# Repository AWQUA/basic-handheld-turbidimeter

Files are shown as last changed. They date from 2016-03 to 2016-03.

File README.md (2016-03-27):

#Basic Handheld Turbidimeter
##Purpose  
The Basic Handheld Turbidimeter is designed to measure turbidity on demand, portably, for the lowest possible price.  

##Function  
_How does the device measure a parameter?_  
This device is a single-beam [nephelometrer](https://en.wikipedia.org/wiki/Nephelometer). Light from an infrared light-emitting diode (IR LED) is scattered by suspended sediment as it passes through a sample of water. This scattered light is detected by an IR-sensitive [photodiode](https://en.wikipedia.org/wiki/Photodiode) mounted at a right angle to the center of the IR LED's light beam. The intensity of light detected by the photodiode is referenced to a calibration curve stored in the device's memory to interpolate the corresponding turbidity value, measured in [nephelometric turbidity units (NTU)](http://or.water.usgs.gov/grapher/fnu.html).  

_How does the device record data?_  
This device is intended for basic manual operation and does not contain storage for data.   

_How does the device display data?_  
The microcontroller at the heart of this device reads the frequency of pulses transmitted by the [photodiode unit](http://www.mouser.com/ProductDetail/ams/TSL230BRD-TR/?qs=sGAEpiMZZMu97qiQi8P%252buifvOPr%252b402N67DKHn09PFo%3d), interpolates the turbidity value from stored calibration data, and displays the turbidity value on a [four-digit display panel](http://www.electrodragon.com/product/7-segment-4-digit-display-common-anode/) (much like those used in some alarm clocks).

_What units does the device report in?_  
Like all AWQUA turbidimeters, this device reports readings in  [nephelometric turbidity units (NTU)](http://or.water.usgs.gov/grapher/fnu.html).  

_How does the device communicate data electronically?_  
This device does not possess data telemetry capabilities.  

##Use Case  
_Where can the device be safely used?_  
This device can handle temperatures up to 70C, and is intended for field conditions. It is not water proof or water resistent, however.

##Power  
_How is the device powered?_  
This device uses 3.3V DC power, and requires less than 100mA of current. A standard 3.7V lithium ion or polymer battery, or three AA alkaline batteries, would suffice to power it.

_How much power does it use?_  
In semi-automated testing, this device was capable of taking 5000 measurements on one set of three AA batteries.

##Standard and Testing  
_How was the device tested?_  
Testing procedures for this device are described in full in [An Affordable Open-Source Turbidimeter](http://www.mdpi.com/1424-8220/14/4/7142).

_How did it perform?_  
Testing results for this device are described in full in [An Affordable Open-Source Turbidimeter](http://www.mdpi.com/1424-8220/14/4/7142). The figure below shows the performance of this model of device, versus a popular commercial turbidimeter.  
"Basic Handheld Turbidimeter evaluated against commercial equivalent"

_What performance standards does the device meet?_  
This device was designed and successfully tested to reliably measure turbidity values well below 1.0 NTU, which is the maximum turbidity value recommended by the World Health Organization for drinking water prior to disinfection. Please note however that this device is not certified to meet EPA requirements for the routine turbidity monitoring of treated drinking water in the United States. 

_What monitoring standards can this device be used to meet?_  
This device is one of several proven turbidimeter designs out there that can be used to meet international and World Health Organization guidelines on turbidity monitoring, yet are not able to meet the very exacting (and expensive) American and European turbidity detection standards. There is an urgent global need for simple, affordable turbidity detection, and AWQUA members are working to establish alternative turbidity detection standards to address this need. Please check out our [Standards](https://github.com/AWQUA/Standards) repository for more information.

##Construction  

###Bill of Materials
| Quantity  | Part Description | Example Price (each) |
| :-------------: | ------------- | :-------------: |
| 1 | ATMega328P-PU microprocessor  | [$2.90](http://www.electrodragon.com/product/atmega328-with-arduino-optiboot-uno/)|
| 1 | 4-digit, 7-segment display  | [$2.10](http://www.electrodragon.com/product/7-segment-4-digit-display-common-anode/)|
| 1 | 74HC595 shift register  | [$0.62](http://www.mouser.com/ProductDetail/Texas-Instruments/SN74HC595N/?qs=sGAEpiMZZMuyBeSSR239IeaeNSzgQbS%2f1btldJdqa6k%3d) |
| 1 | LMT86 temperature sensor  | [$1.00](http://www.mouser.com/ProductDetail/Texas-Instruments/LMT86LP/?qs=sGAEpiMZZMvfFCidbTccA1jyVRrxk5nB%252bTEjPRynSGM%3d)|
| 1 | TSL230BRD  | [$4.83](http://www.mouser.com/ProductDetail/ams/TSL230BRD-TR/?qs=sGAEpiMZZMu97qiQi8P%252buifvOPr%252b402N67DKHn09PFo%3d)|
| 1 | LF33ABV 3.3V Voltage regulator  | [$1.03](http://www.mouser.com/ProductDetail/STMicroelectronics/LF33ABV/?qs=sGAEpiMZZMsGz1a6aV8DcBQiArhhid1gDswAeAw%2fIB0%3d)|
| 2 | 10uF aluminum electrolytic capacitors  | [$0.24](http://www.mouser.com/ProductDetail/Nichicon/ULD1J100MDD1TD/?qs=sGAEpiMZZMvwFf0viD3Y3c1N%2fF%2fpDmX12XlNW9X9Y3vZmYyMo5GpOw%3d%3d)|
| 2 | 22pF ceramic capacitors  | [$0.03](http://www.mouser.com/ProductDetail/Vishay-BC-Components/K220J10C0GF5UH5/?qs=sGAEpiMZZMsh%252b1woXyUXj9nJp%252b8gphztXIKBUu3gv%252bs%3d)|
| 5 | 100nF ceramic capacitors  | [$0.06](http://www.mouser.com/ProductDetail/Vishay-BC-Components/K104Z15Y5VE5TL2/?qs=sGAEpiMZZMsh%252b1woXyUXj5VNmf0jXPWIrWjnp1zAXac%3d)|
| 4 | 100 ohm resistors  | [$0.10](http://www.mouser.com/ProductDetail/KOA-Speer/MOS1-2CT52R101J/?qs=sGAEpiMZZMtlubZbdhIBICYVxaT5CDYBpEIIN%2f0BoAk%3d)|
| 1 | 220 ohm resistors  | [$0.10](http://www.mouser.com/ProductDetail/KOA-Speer/MOS1-2CT52R221J/?qs=sGAEpiMZZMtlubZbdhIBICYVxaT5CDYBStqm8FrIljg%3d)|
| 1 | 1K ohm resistors 1% tolerance | [$0.10](http://www.mouser.com/ProductDetail/Vishay-Beyschlag/MBB02070C1001FCT00/?qs=sGAEpiMZZMtlubZbdhIBIAA6NYEPHyksoxlYyK2s%252btM%3d)|
| 4 | 10K ohm resistors  | [$0.10](http://www.mouser.com/ProductDetail/Vishay-Beyschlag/MBA02040C1002FCT00/?qs=sGAEpiMZZMtlubZbdhIBIP7908E9uONJr6Tgqqo7oLA%3d)|
| 1 | IR LED  | [$0.47](http://www.mouser.com/ProductDetail/Kingbright/WP7113SF4C/?qs=sGAEpiMZZMvAL21a%2fDhxMro1KOf4QOs%252bCw5JRgjZK8o%3d)|
| 1 | LED lighting driver | [$0.54](http://www.mouser.com/Search/ProductDetail.aspx?R=AL5809-30S1-7virtualkey62110000virtualkey621-AL5809-30S1-7)|
| 1 | Momentary contact button  | [$0.91](http://www.mouser.com/ProductDetail/Mountain-Switch/104-0013-EVX/?qs=sGAEpiMZZMvxtGF7dlGNpr35VnaTB25ys95hy84%252ba4o%3d)|
| 1 | SPST power switch  | [$1.15](http://www.mouser.com/ProductDetail/CHERRY/TRG22F2FBBNN/?qs=sGAEpiMZZMtNT9UGfLL4eOd3cDQgL8vM5i2VNLX9H3E%3d)|
| 100 | Header pins (0.1" spacing)  | [$.00225](http://www.electrodragon.com/product/break-away-header/)|
|||
||**Total Cost:**|**$17.61**|
###Circuit Board
####Schematic
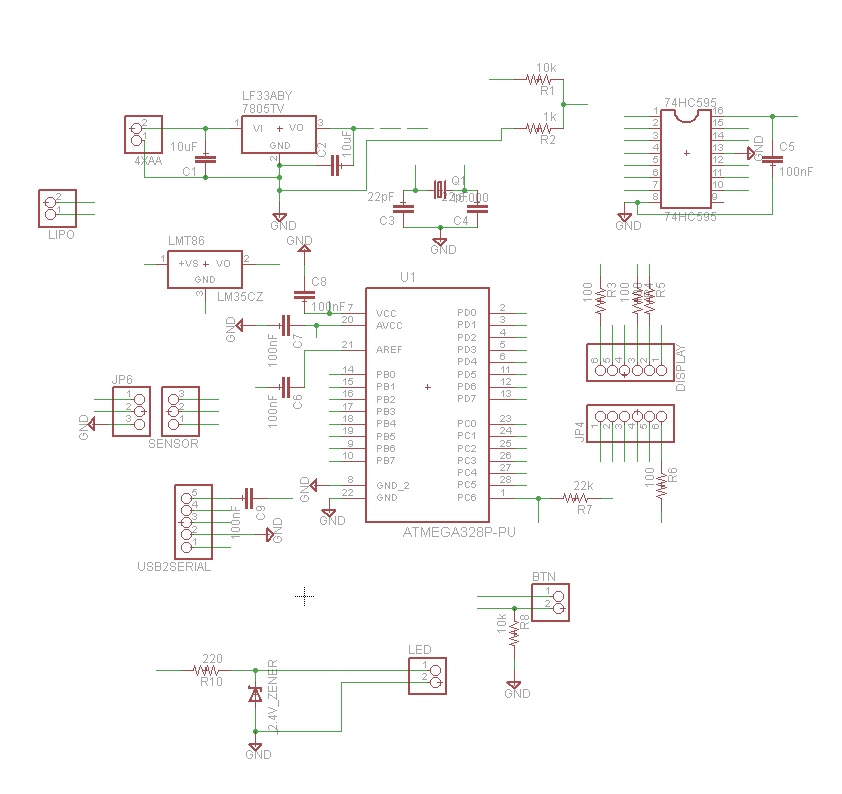
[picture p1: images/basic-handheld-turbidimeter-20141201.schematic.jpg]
picture alt Schematic of Basic Handheld Turbidimeter circuit board [2014-12-01]

####Layout
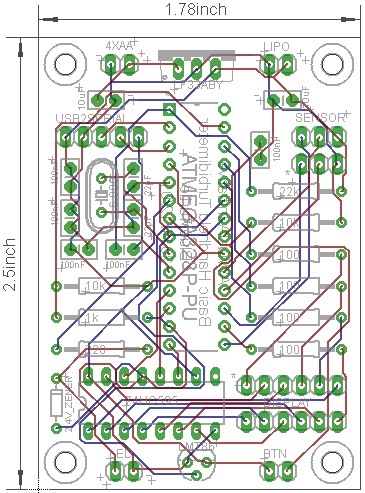
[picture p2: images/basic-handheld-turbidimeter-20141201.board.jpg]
picture alt Layout of Basic Handheld Turbidimeter circuit board [2014-12-01]

###Assembly
For assembly instructions, see the [Supplementary Materials](http://www.mdpi.com/1424-8220/14/4/7142/s1) for An Affordable Open-Source Turbidimeter.  
##FAQ and Troubleshooting  
###Online Resources

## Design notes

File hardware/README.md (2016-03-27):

#Hardware
There are up to three boards in the `basic-handheld-turbidimeter`: the main board (housing the microprocessor), a sensor board that connects to the main board through 0.1" header pins, and an optional third board that lets the display plug directly in to the main board.

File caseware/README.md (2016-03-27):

#Caseware
The caseware for the `basic-handheld-turbidimeter` is provided as an SVG file and a FreeCAD python macro (FCMacro) -- the first file may be viewed and edited in many vector graphics programs (e.g. [Inkscape](https://inkscape.org/en/)), and the latter in [FreeCAD](http://www.freecadweb.org/).  
  
This case is designed for 0.25"-thick acryllic; suitable alternative materials exist. It is recommended that the case be cut from an opaque material to prevent background light leakage onto the turbidity sensor (though can be programmed to compensate for this to an extent), with the exception of the `case_top_cover` piece (bottom left in the SVG layout) which should be cut from a clear material so that the LED display underneath it is visible to the user.

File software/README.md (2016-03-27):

#Software
The software for this device is kept here; it requires the following external libraries to compile properly:

[`EEPROM`](https://www.arduino.cc/en/Reference/EEPROM)
[`EEPROMWriteAnything.h`](http://playground.arduino.cc/Code/EEPROMWriteAnything)
[`PinChangeInt`](http://playground.arduino.cc/Main/PinChangeInt)

To edit this code in the [Arduino IDE](https://www.arduino.cc/en/Main/Software), copy the folder named basic-handheld-turbidimeter into your Arduino sketchbook.

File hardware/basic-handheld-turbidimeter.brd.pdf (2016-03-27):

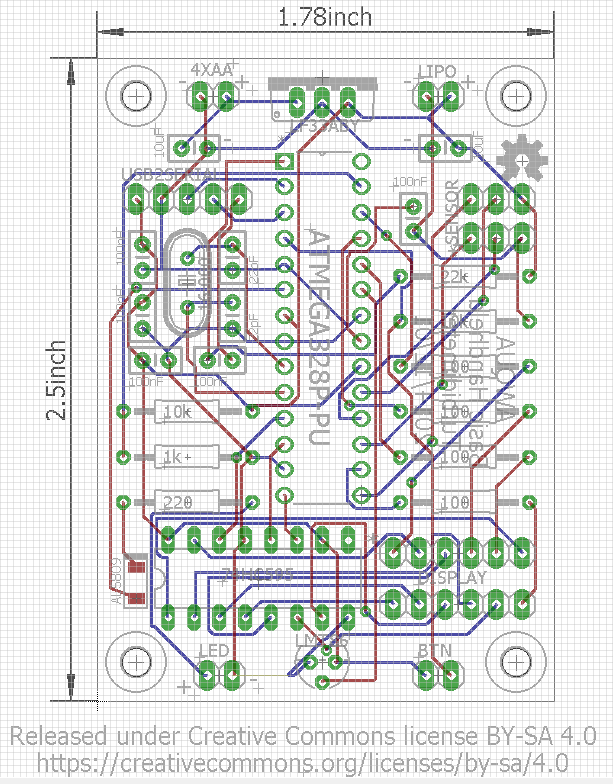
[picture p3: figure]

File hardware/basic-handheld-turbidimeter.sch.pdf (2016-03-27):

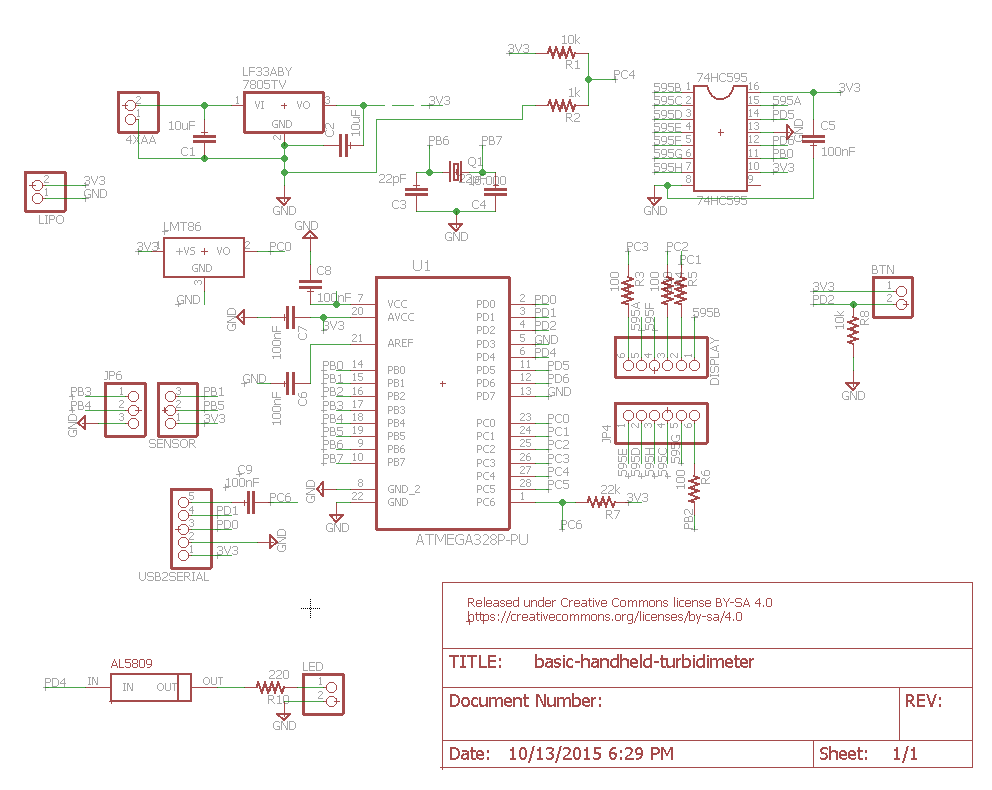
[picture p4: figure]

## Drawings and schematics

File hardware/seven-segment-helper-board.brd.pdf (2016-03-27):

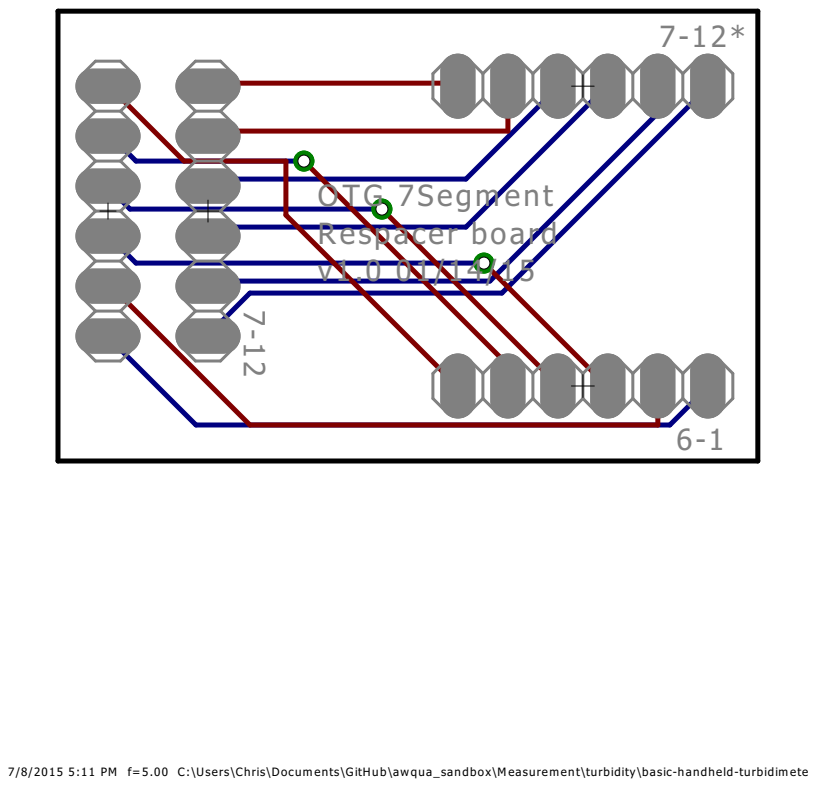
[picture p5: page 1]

7/8/2015 5:11 PM f=5.00 C:\Users\Chris\Documents\GitHub\awqua_sandbox\Measurement\turbidity\basic-handheld-turbidimeter\hardware\seven-segment-helper-boardsch.brd

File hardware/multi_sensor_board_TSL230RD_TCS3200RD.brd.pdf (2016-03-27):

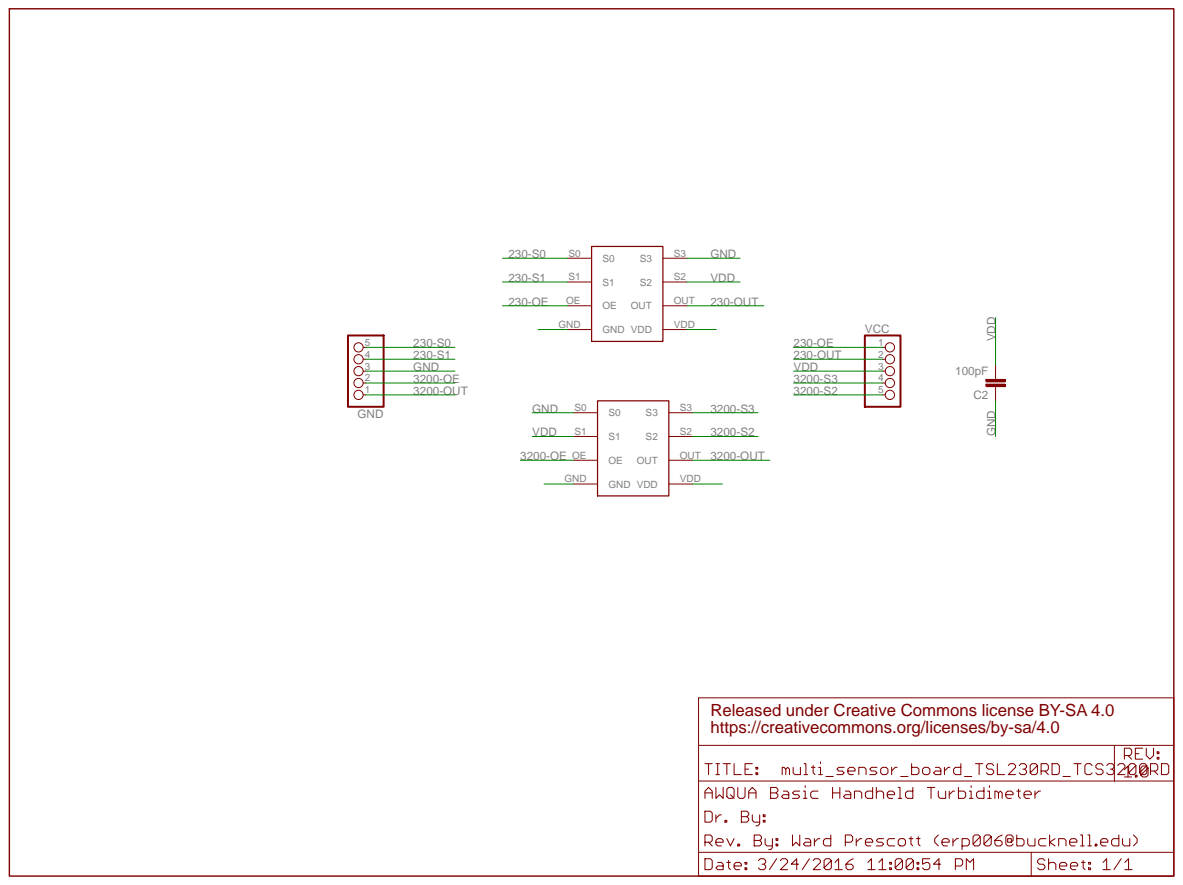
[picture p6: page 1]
GND GND; OUT; VDD; GND; VCC 1 2 3 4; 230-OUT; 3200-OUT

Released under Creative Commons license BY-SA 4.0
https://creativecommons.org/licenses/by-sa/4.0

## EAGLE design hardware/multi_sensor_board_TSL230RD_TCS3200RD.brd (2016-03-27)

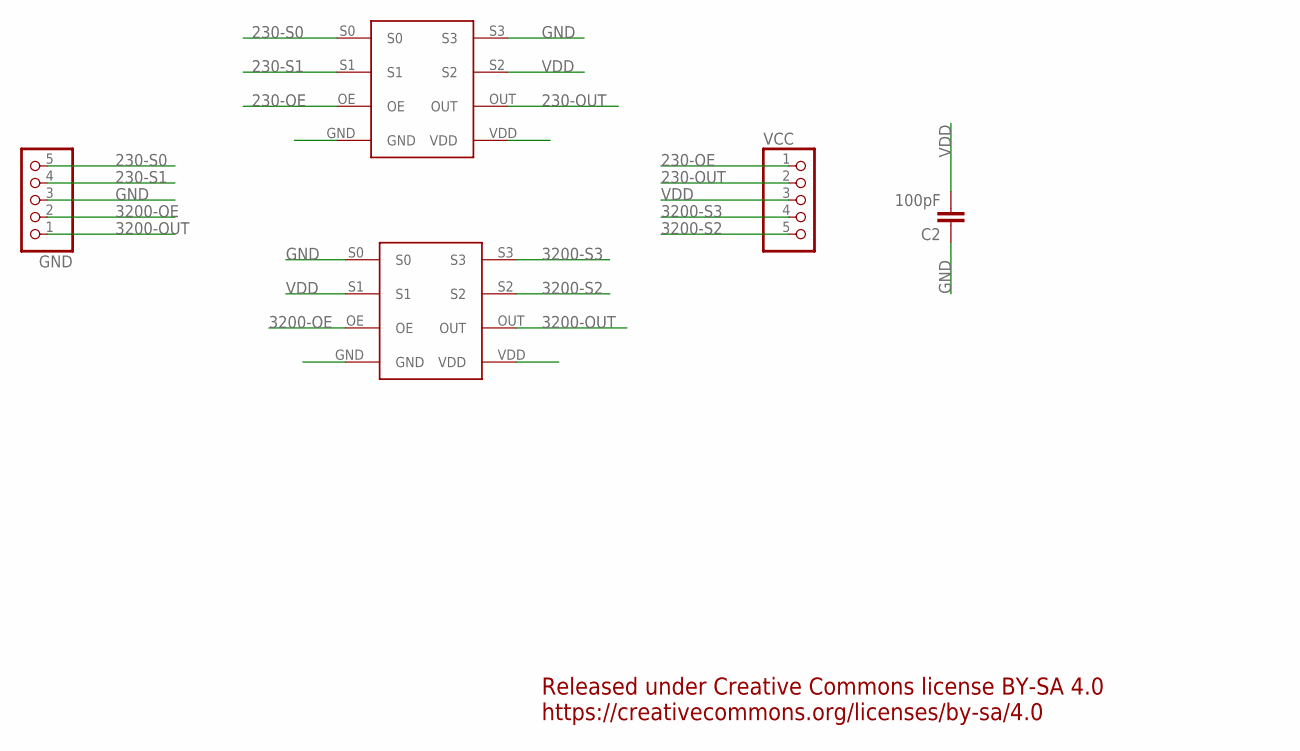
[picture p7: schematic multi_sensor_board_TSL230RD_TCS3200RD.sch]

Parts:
C2: 100pF; 0805
COLOR: TCS3200RD; TSL230RD
GND: PINHD-1X5; 1X05
IR: TSL230R; TSL230RD
VCC: PINHD-1X5; 1X05

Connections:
230-OE: IR.OE, VCC.1
230-OUT: IR.OUT, VCC.2
230-S0: GND.5, IR.S0
230-S1: GND.4, IR.S1
3200-OE: COLOR.OE, GND.2
3200-OUT: COLOR.OUT, GND.1
3200-S2: COLOR.S2, VCC.5
3200-S3: COLOR.S3, VCC.4
GND: C2.1, COLOR.GND, COLOR.S0, GND.3, IR.GND, IR.S3
VDD: C2.2, COLOR.S1, COLOR.VDD, IR.S2, IR.VDD, VCC.3

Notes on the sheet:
Released under Creative Commons license BY-SA 4.0 https://creativecommons.org/licenses/by-sa/4.0

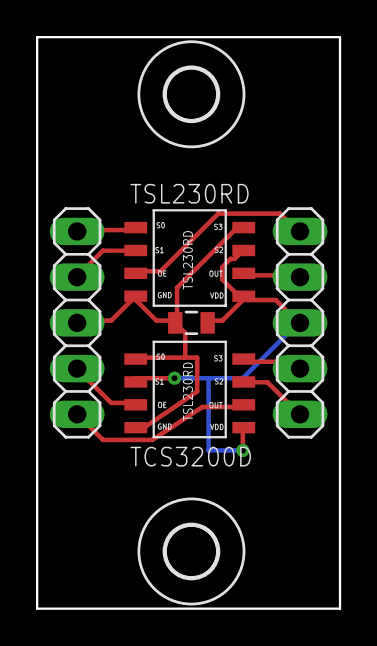
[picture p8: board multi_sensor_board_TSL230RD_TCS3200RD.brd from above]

Board: 2 copper layers, 16.8 x 31.8 mm, 7 parts (0 on the bottom side), 10 nets.

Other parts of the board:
U$1, U$2: 2,8

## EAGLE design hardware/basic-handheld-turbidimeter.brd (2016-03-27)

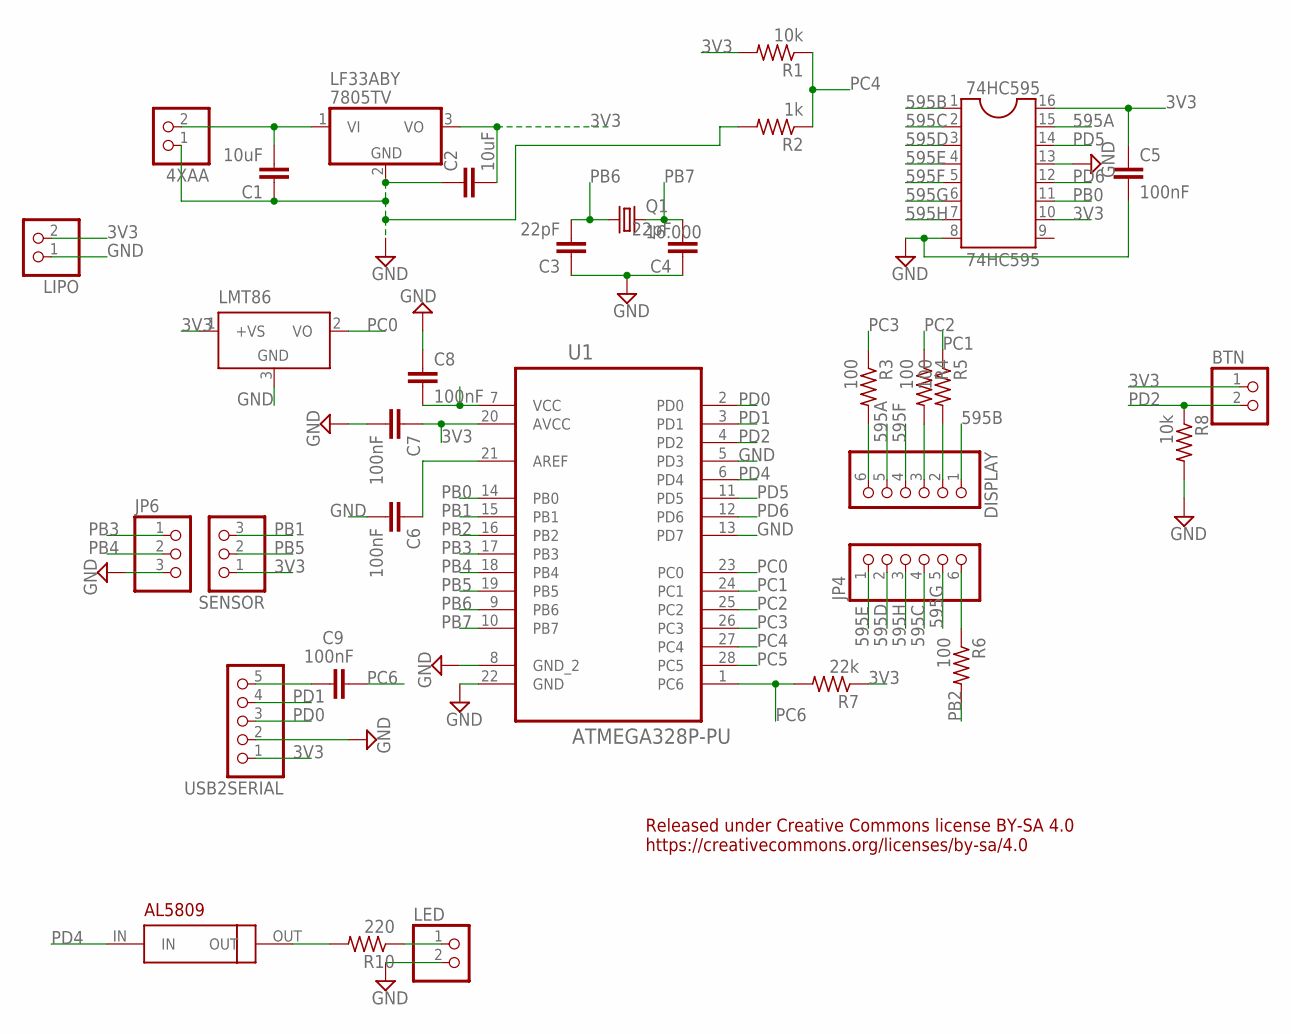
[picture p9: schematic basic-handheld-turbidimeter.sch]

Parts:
4XAA: PINHD-1X2; 1X02
74HC595: 74HC595; DIL16
BTN: PINHD-1X2; 1X02
C1, C2: 10uF; CAP-PTH-SMALLEZ
C3, C4: 22pF; CAP-PTH-SMALLEZ
C5, C6, C7, C8, C9: 100nF; CAP-PTH-SMALLEZ
DISPLAY: PINHD-1X6; 1X06
JP4: PINHD-1X6; 1X06
JP6: PINHD-1X3; 1X03
LED: PINHD-1X2; 1X02
LF33ABY: 7805TV; TO220V
LIPO: PINHD-1X2; 1X02
LMT86: LM35CZ; TO92
Q1: 16.000; HC49/S
R1, R8: 10k; 0207/12
R2: 1k; 0207/12
R3, R4, R5, R6: 100; 0207/12
R7: 22k; 0207/12
R10: 220; 0207/12
SENSOR: PINHD-1X3; 1X03
U1: ATMEGA328P-PU; DIP254P762X457-28
U$6: AL5809
USB2SERIAL: PINHD-1X5; 1X05

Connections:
3V3: 74HC595.10, 74HC595.16, BTN.1, C2.2, C5.1, C7.1, C8.2, LF33ABY.3 (VO), LIPO.2, LMT86.1 (+VS), R1.2, R7.1, SENSOR.1, U1.7 (VCC), U1.20 (AVCC), USB2SERIAL.1
595A: 74HC595.15, DISPLAY.5
595B: 74HC595.1, DISPLAY.1
595C: 74HC595.2, JP4.4
595D: 74HC595.3, JP4.2
595E: 74HC595.4, JP4.1
595F: 74HC595.5, DISPLAY.4
595G: 74HC595.6, JP4.5
595H: 74HC595.7, JP4.3
GND: 4XAA.1, 74HC595.8, 74HC595.13, C1.1, C2.1, C3.1, C4.1, C5.2, C6.2, C7.2, C8.1, JP6.3, LED.2, LF33ABY.2 (GND), LIPO.1, LMT86.3 (GND), R2.2, R8.2, U1.5 (PD3), U1.8 (GND_2), U1.13 (PD7), U1.22 (GND), USB2SERIAL.2
LED: LED.1, R10.1
unnamed: 4XAA.2, C1.2, LF33ABY.1 (VI)
unnamed: R10.2, U$6.OUT
unnamed: C6.1, U1.21 (AREF)
unnamed: C9.2, USB2SERIAL.5
unnamed: DISPLAY.6, R3.2
unnamed: DISPLAY.3, R4.2
unnamed: DISPLAY.2, R5.2
unnamed: JP4.6, R6.1
PB0: 74HC595.11, U1.14 (PB0)
PB1: SENSOR.3, U1.15 (PB1)
PB2: R6.2, U1.16 (PB2)
PB3: JP6.1, U1.17 (PB3)
PB4: JP6.2, U1.18 (PB4)
PB5: SENSOR.2, U1.19 (PB5)
PB6: C3.2, Q1.1, U1.9 (PB6)
PB7: C4.2, Q1.2, U1.10 (PB7)
PC0: LMT86.2 (VO), U1.23 (PC0)
PC1: R5.1, U1.24 (PC1)
PC2: R4.1, U1.25 (PC2)
PC3: R3.1, U1.26 (PC3)
PC4: R1.1, R2.1, U1.27 (PC4)
PC5: U1.28 (PC5)
PC6: C9.1, R7.2, U1.1 (PC6)
PD0: U1.2 (PD0), USB2SERIAL.3
PD1: U1.3 (PD1), USB2SERIAL.4
PD2: BTN.2, R8.1, U1.4 (PD2)
PD4: U1.6 (PD4), U$6.IN
PD5: 74HC595.14, U1.11 (PD5)
PD6: 74HC595.12, U1.12 (PD6)

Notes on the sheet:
Released under Creative Commons license BY-SA 4.0 https://creativecommons.org/licenses/by-sa/4.0

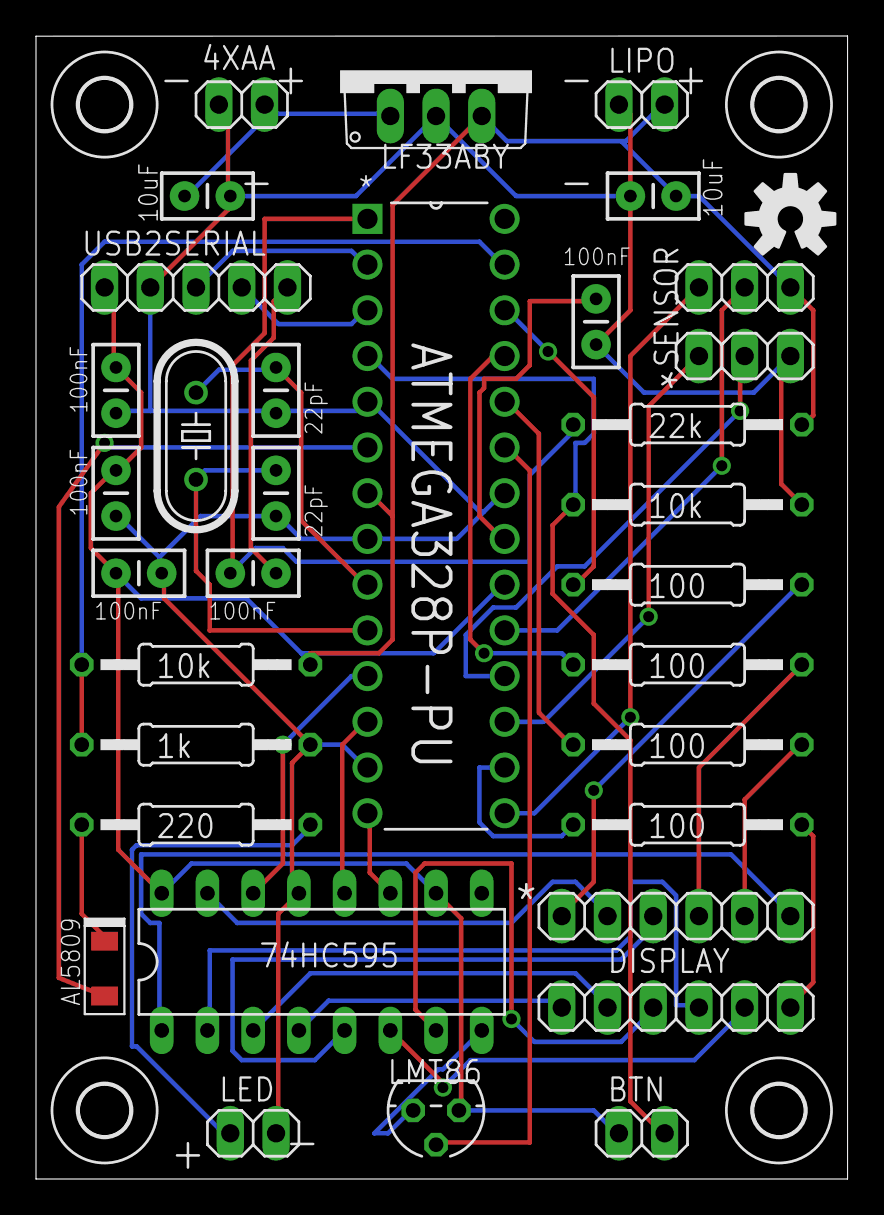
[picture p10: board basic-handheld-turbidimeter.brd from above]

Board: 2 copper layers, 45.1 x 63.5 mm, 38 parts (0 on the bottom side), 39 nets.

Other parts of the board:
U$1, U$2, U$3, U$4: 2,8
U$5: OSHW-LOGO-M

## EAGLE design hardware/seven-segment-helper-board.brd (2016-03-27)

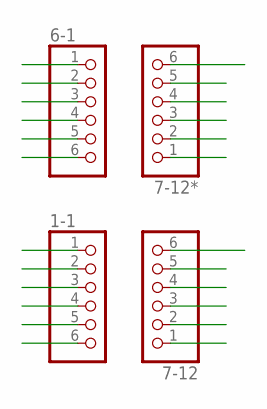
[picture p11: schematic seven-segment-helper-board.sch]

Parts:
1-1, 6-1, 7-12, 7-12*: PINHD-1X6; 1X06

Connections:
1: 1-1.1, 6-1.1
2: 1-1.2, 6-1.2
3: 1-1.3, 6-1.3
4: 1-1.4, 6-1.4
5: 1-1.5, 6-1.5
6: 1-1.6, 6-1.6
7: 7-12.1, 7-12*.1
8: 7-12.2, 7-12*.2
9: 7-12.3, 7-12*.3
10: 7-12.4, 7-12*.4
11: 7-12.5, 7-12*.5
12: 7-12.6, 7-12*.6

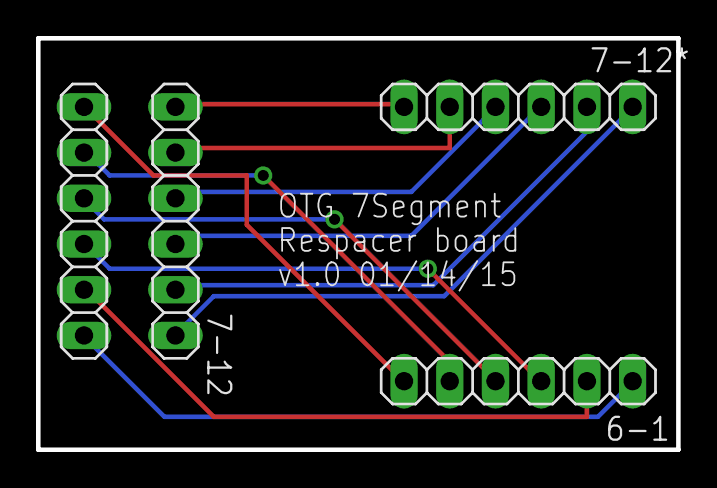
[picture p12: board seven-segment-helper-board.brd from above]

Board: 2 copper layers, 35.6 x 22.9 mm, 4 parts (0 on the bottom side), 12 nets.

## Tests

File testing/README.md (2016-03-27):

#Testing
An academic evaluation of an earlier version of the `basic-handheld-turbidimeter` was published in the open-access journal [Sensors](http://www.mdpi.com/1424-8220/14/4/7142); the article and supplementary materials are included in this folder.

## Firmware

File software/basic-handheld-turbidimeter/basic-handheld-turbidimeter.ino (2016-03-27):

 
/*--------------------------OPEN TURBIDIMETER PROJECT------------------------*/
/*
Copyright 2012-2014 Alex Krolick and Chris Kelley

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
    You should have received a copy of the GNU General Public License
    along with this program.  If not, see <http://www.gnu.org/licenses/>.
*/
/*------------------------------- ARDUINO CODE ------------------------------*/

// Flags
boolean debug = false;  // IMPORTANT: to update EEPROM, change this to true
boolean using_modem = false; // if not using a GSM modem, change to false
boolean using_bluetooth = false; //
long debug_rep_count = 0;

// Libraries
// NOTE: Be sure to use the libraries included with this sketch
// (by placing them in your Arduino or Sketchbook folder)
#include <PinChangeInt.h>
#include <EEPROM.h>
#include <EEPROMAnything.h>
boolean common_cathode_display = true; //if using a common-anode seven segment display, change to false
boolean button_resting_low = false;

/*if using common_cathode_display, uncomment the two lines below, and comment the two lines below those*/
#define COUNT_SEVEN_SEG_NUMBERS  13
#define COUNT_SEVEN_SEG_LETTERS   9
#define SEVEN_SEG_NUMBERS {B11000000,  B11111001,  B10100100,  B10110000, B10011001,  B10010010,  B10000010,  B11111000, B10000000,  B10010000,  B01111111,  B10111111, B11111111}
#define SEVEN_SEG_LETTERS {B10101111,  B10000110,  B10100001,  B10010001, B11000111,  B10010010,  B10000111,  B11000000, B11100011}

/*otherwise, use this*/
//#define SEVEN_SEG_NUMBERS {B00111111,  B00000110,  B01011011,  B01001111, B01100110,  B01101101,  B01111101,  B00000111, B01111111,  B01101111,  B10000000,  B01000000, B00000000}
//#define SEVEN_SEG_LETTERS {B01010000,  B01111001,  B01011110,  B01101110, B00111000,  B01101101,  B01111000,  B00111111, B00011100}

//Definitions
#define IR_LED           4
#define TSL_S1          12
#define TSL_S0          11
#define TSL_FREQ_PIN    13
#define TSL_OE           9
#define BPIN             2    // external button
#define VPIN            A4    // read voltage from this pin
#define SHIFT_CLOCK_PIN  8
#define SHIFT_DATA_PIN   5
#define SHIFT_LATCH_PIN  6
#define TPIN            A0 
#define DIV_R1       10000   // resistance for R1
#define DIV_R2        1000   // resistance for R2
#define VDIV      0.090909
#define HIGH_SENSITIVITY  100
#define MED_SENSITIVITY    10   
#define LOW_SENSITIVITY     1     
#define HIGH_SCALE          2
#define SAMPLING_WINDOW   500
#define READ_REPS           8

boolean button_pressed = false, sufficient_battery = true;
volatile unsigned long pulse_count, timer;
int scale_divider = HIGH_SCALE, sensitivity = HIGH_SENSITIVITY, btn_press = 0, btn_press_threshold = 50;
float div_fact = 1.0, system_voltage = 0.0, humidity, temperature;

boolean over_flag = false;

const int num_displays = 4;                                  
const int shift_latch = SHIFT_LATCH_PIN;  // RCLK                           
const int shift_clock = SHIFT_CLOCK_PIN;  // SRCLCK
const int shift_data = SHIFT_DATA_PIN;   // SER
const int dispPorts[num_displays] = {A3,A2,A1,10};
String language = "english";
const byte SevenSegNumbers[COUNT_SEVEN_SEG_NUMBERS] = SEVEN_SEG_NUMBERS;
const byte SevenSegLetters[COUNT_SEVEN_SEG_LETTERS] = SEVEN_SEG_LETTERS;

struct config_t{
  int foo;           
  long machine_id;   
  unsigned long last_calibration_timestamp; 
  float y0, y1, y2, y3, a0, b0, c0, a1, b1, c1, a2, b2, c2;
}
config;

void setup() { 
  analogReference(INTERNAL); 
  delay(50);
  pinMode(TSL_OE, OUTPUT);
  pinMode(TSL_FREQ_PIN, INPUT);
  pinMode(TSL_S0, OUTPUT);  
  pinMode(TSL_S1, OUTPUT);
  pinMode(IR_LED, OUTPUT);
  pinMode(TPIN, INPUT);
  pinMode(BPIN, INPUT);
  digitalWrite(TSL_OE, LOW);
  digitalWrite(TSL_S0, HIGH);
  digitalWrite(TSL_S1, HIGH);
  digitalWrite(IR_LED, LOW);
  pinMode(shift_latch, OUTPUT); // shift register
  pinMode(shift_clock, OUTPUT); // shift register
  pinMode(shift_data,  OUTPUT); // shift register
  for(int i = 0; i < num_displays; i++){ 
    pinMode(dispPorts[i], OUTPUT); 
  }

  if(debug){
    config.foo = 255; //EEPROMAnything seems to need the struct to start with a integer in [0,255]
    config.machine_id = 11111111; //example
    config.last_calibration_timestamp = 1390936721;  //example


  //PLEASE NOTE -- the coefficients below are merely reasonable examples. 
  //Your device WILL require a calibration to determine the proper coefficient values.
    config.y0 = 0;
    config.a0 = 0.00007391;
    config.b0 = 0.07836;
    config.c0 = -46.096;
    config.y1 = 660;
    config.a1 = 0.00000773;
    config.b1 = 0.2315;
    config.c1 = -226.3;
    config.y2 = 2700;
    config.a2 = -0.00000678;
    config.b2 = 0.2315;
    config.c2 = -226.3;
    config.y3 = 6522;
    
    EEPROM_writeAnything(0, config);
  }
  else{ EEPROM_readAnything(0, config); }


  if(debug){
    Serial.begin(9600);
    Serial.println("starting...");
  }
  temperature = readTemperature();
  btn_press_threshold = 1;
  pulse_count = 0;
  timer = millis();
  turnOffDisplay();
  setSensitivity(sensitivity); // set sensor sensitivity
  timer = millis();
  displayForInterval(-1, "dashes", 1000);
  turnOffDisplay();
  
  if(divisionFactor_TSL230R() < 0){
    sufficient_battery = false;
    displayForInterval(-1, "error", 2000);
  }else{
   displayForInterval(-1, "ready", 2000);
   turnOffDisplay();
  }

  Serial.println("entering loop...");
}

void loop() {
  if(sufficient_battery){
    delay(5);
    readTemperature();
    delay(5);
    //Serial.println(readTemperature());
    if(digitalRead(BPIN) != btn_press){
      btn_press = digitalRead(BPIN);
      Serial.print("new button value: ");
      Serial.println(btn_press);
    }
    if (btn_press == btn_press_threshold){  //digital logic (1 = button press)
      button_pressed = true;
      divisionFactor_TSL230R();                
      // read, but discard first reading
      div_fact = divisionFactor_TSL230R(); 
      Serial.print("division factor: "); 
      Serial.println(div_fact);
      if(div_fact < 0){sufficient_battery = false;}     
      else{
        // Given there is enough battery power for the  sensor,
        // - read sensor value for given number of times,
        // - display the resulting value for 4000 milliseconds,
        // - clear out register pins, for a clean display next 
        //   time device is powered off/on.
        // - build a text message and transmit, 
        //   if using_modem flag is set to true.     
        debug_rep_count++;
        //display_voltage();
        //display_rep_count(debug_rep_count);
        displayForInterval(-1, "cycle_dashes", 1000);
        float reading = takeReadings(READ_REPS);
        if(debug){
          Serial.print("output:");
          Serial.println(reading);
        }
        if(over_flag){
          for(int z = 0; z < 6; z++){
            displayForInterval(reading, "data",500);
            displayForInterval(-1, "clear", 300);            
          }
          over_flag = false;
        }
      else{displayForInterval(reading, "data",2000);}
        displayForInterval(-1, "clear", 100);
      }
    }
    if(button_pressed){
      button_pressed = false; // reset
      turnOffDisplay();
    }
  }
  else{
    divisionFactor_TSL230R();
    displayForInterval(-1, "error", 500);
    turnOffDisplay();
    delay(5000);
    display_rep_count(debug_rep_count);
    display_voltage();
  }

}
/*--------------------------Debug Functions---------------------------*/
void display_rep_count(int debug_rep_count){
  unsigned long timer2 = millis();
  while(millis() - timer2 < 500){
    DisplayADigit(dispPorts[0],byte(SevenSegLetters[0]));  //r
    delay(2);
  }
  displayForInterval(debug_rep_count, "data",500);
}

void display_voltage(){
  unsigned long timer2 = millis();
  while(millis() - timer2 < 500){
    DisplayADigit(dispPorts[0],byte(SevenSegLetters[8]));  //u
    delay(2);
  }
  displayForInterval(getVoltageLevel(), "data",500);
}
/*--------------------------Sensor Functions--------------------------*/
void add_pulse() {pulse_count++;}

float takeReadings(int num_rdgs){
  Serial.println("entered readings function");
  int rep_cnt = 0, b = 0;
  long sum = 0, low = 1000000, high = 0, rd = 0;
  PCintPort::attachInterrupt(TSL_FREQ_PIN, add_pulse, RISING);  
  Serial.println("attached interrupt");
  delay(200);
  pulse_count = 0; //reset frequency counter
  timer = millis();
  Serial.println("readings:");
  
  boolean take_dark_counts = true;
  int throwaway_rdng_cnt = 5;
  rep_cnt = 0;
  sum = 0;
  digitalWrite(IR_LED, HIGH);
  delay(10);
  while(rep_cnt < num_rdgs + throwaway_rdng_cnt){
    if(millis() - timer >= SAMPLING_WINDOW){    
      rd = pulse_count * scale_divider;
      if(rep_cnt < throwaway_rdng_cnt){
          Serial.print("throwaway reading: ");
          Serial.println(rd);
      }else{
        if(take_dark_counts){// take dark count reading
          digitalWrite(IR_LED, LOW);
          delay(10);
          timer = millis();     //update timer
          pulse_count = 0;
          while(millis() - timer < SAMPLING_WINDOW){;}
          rd -= pulse_count * scale_divider;
          Serial.println(rd);
          digitalWrite(IR_LED, HIGH);
          delay(10);
        }else{
          Serial.println(rd);
        }
        if(rd > high){high = rd;}                 
        if(rd < low){low = rd;}
        sum += rd;            //sum the readings
      }
      timer = millis();     //update timer
      rep_cnt++;
      pulse_count = 0;
    }  
  }  
  PCintPort::detachInterrupt(TSL_FREQ_PIN);            //turn off frequency-counting function
  digitalWrite(IR_LED, LOW);                           //turn off light source
  //chuck out highest and lowest readings and average the rest, if there are four or more readings
  if(num_rdgs > 3){                  
    sum -= (high + low);
    b = 2;
  }
  float d_f = divisionFactor_TSL230R();
  Serial.print("sensor division factor:");
  Serial.println(d_f);
  Serial.print("light count average: ");
  Serial.println(float(sum) / float(num_rdgs - b));
  Serial.print("factored count: ");
  
  float raw_value = float(sum) / float(num_rdgs - b) / d_f;
  float ntu_value = -1;
  Serial.println(raw_value);
  if(sensitivity == HIGH_SENSITIVITY){
    if(raw_value > config.y3)       {;}//use this to raise an alarm -- for example, if the value is beyond the range the device is calibrated to measure
    if(raw_value > config.y2)       { ntu_value = raw_value * (raw_value * config.a2 + config.b2) + config.c2; }  
    else if(raw_value > config.y1)  { ntu_value = raw_value * (raw_value * config.a1 + config.b1) + config.c1; }
    else                            { ntu_value = raw_value * (raw_value * config.a0 + config.b0) + config.c0; }
    
    if(ntu_value < 0.00){ntu_value = 0.00;}
    if(ntu_value > 9999){ntu_value = 9999;}
    return ntu_value;
  }
  else{return 9999;}
}

void setSensitivity(int sens){    //set sensor sensitivity
  if(sens == LOW_SENSITIVITY){  
    digitalWrite(TSL_S0, LOW);
    digitalWrite(TSL_S1, HIGH);
    sensitivity = LOW_SENSITIVITY;
  }
  else if(sens == MED_SENSITIVITY){
    digitalWrite(TSL_S0, HIGH);
    digitalWrite(TSL_S1, LOW);
    sensitivity = MED_SENSITIVITY;
  }
  else if(sens == HIGH_SENSITIVITY){
    digitalWrite(TSL_S0, HIGH);
    digitalWrite(TSL_S1, HIGH);
    sensitivity = HIGH_SENSITIVITY;
  }
  return;
}

/*--------------------------Internal Metering Functions--------------------------*/
float divisionFactor_TSL230R(){
  float m = .0052;   //slope of sensor's linear response curve
  float vmin = 3.0;  //min operating v of sensor
  float vmax = 5.5;  //max operating v of sensor
  float v100 = 4.9;  //voltage | normalized response of TSL230r = 1.0
  float v = getVoltageLevel();
  Serial.print("v*m: ");
  Serial.println(1000 * (4.9 - v) * m);
  if(v < vmin || v > vmax){ return -1; }
  else{ return 1.0 - (4.9 - v) * m; } 
}
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

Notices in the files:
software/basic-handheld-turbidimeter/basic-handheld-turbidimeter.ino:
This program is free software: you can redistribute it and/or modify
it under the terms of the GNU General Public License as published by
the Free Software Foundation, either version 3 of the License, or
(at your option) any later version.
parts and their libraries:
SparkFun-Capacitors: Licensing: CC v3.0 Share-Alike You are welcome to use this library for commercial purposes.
